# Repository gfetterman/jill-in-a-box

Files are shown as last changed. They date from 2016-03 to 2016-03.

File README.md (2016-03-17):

# jill-in-a-box
Audio filtering for the Intan EVAL board ADC inputs

The Intan EVAL board ADC accepts 0 to +3.3V inputs. Jill-in-a-box takes audio signals (+/-3.3V), raises their zero to +1.15V, constrains their amplitude to fit between 0 and +3.3V, and applies a 10kHz anti-aliasing filter.

## Version history
* v1.2: anti-aliaising filter passive components changed to use more common components. Filter cutoff is still 10kHz. Specific changes:
  * R25, R26, R27, R28, R29, R30, R31, R32: were 10kOhm, now 39kOhm
  * C14, C18, C19, C21: were 1000pF, now 270pF
  * C13, C17, C20, C22: were 2000pF, now 560pF
* v1.1: added 2-pole Butterworth anti-aliasing filter, cutoff 10kHz, on each channel
* v1.0: first production version

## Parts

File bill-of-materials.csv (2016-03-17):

Digikey part number | description | quantity
ED1516-ND | TERMINAL BLOCK 3.5MM 4POS PCB | 1
ED2741-ND | TERMINAL BLOCK 3.5MM 3POS PCB | 1
CP-3523SJTR-ND | CONN AUDIO JACK 3.5MM STEREO SMD | 4
LMC6484IN/NOPB-ND | IC OPAMP GP 1.5MHZ RRO 14DIP | 3
RNF14FTD20K0CT-ND | RES 20K OHM 1/4W 1% AXIAL | 8
CF14JT10K0CT-ND | RES 10K OHM 1/4W 5% CARBON FILM | 12
CF14JT39K0CT-ND | RES 39K OHM 1/4W 5% CARBON FILM | 8
CF14JT300RCT-ND | RES 300 OHM 1/4W 5% CARBON FILM | 4
BC1025CT-ND | CAP CER 1000PF 50V 5% RADIAL | 4
BC1018CT-ND | CAP CER 270PF 50V 5% RADIAL | 4
BC1013CT-ND | CAP CER 100PF 50V 5% RADIAL | 4
BC1084CT-ND | CAP CER 0.1UF 50V 10% RADIAL | 6
BC1022CT-ND | CAP CER 560PF 50V 5% RADIAL | 4
H342-ND | Screws 440 | 4
36-8714-ND | Standoffs 440 | 4

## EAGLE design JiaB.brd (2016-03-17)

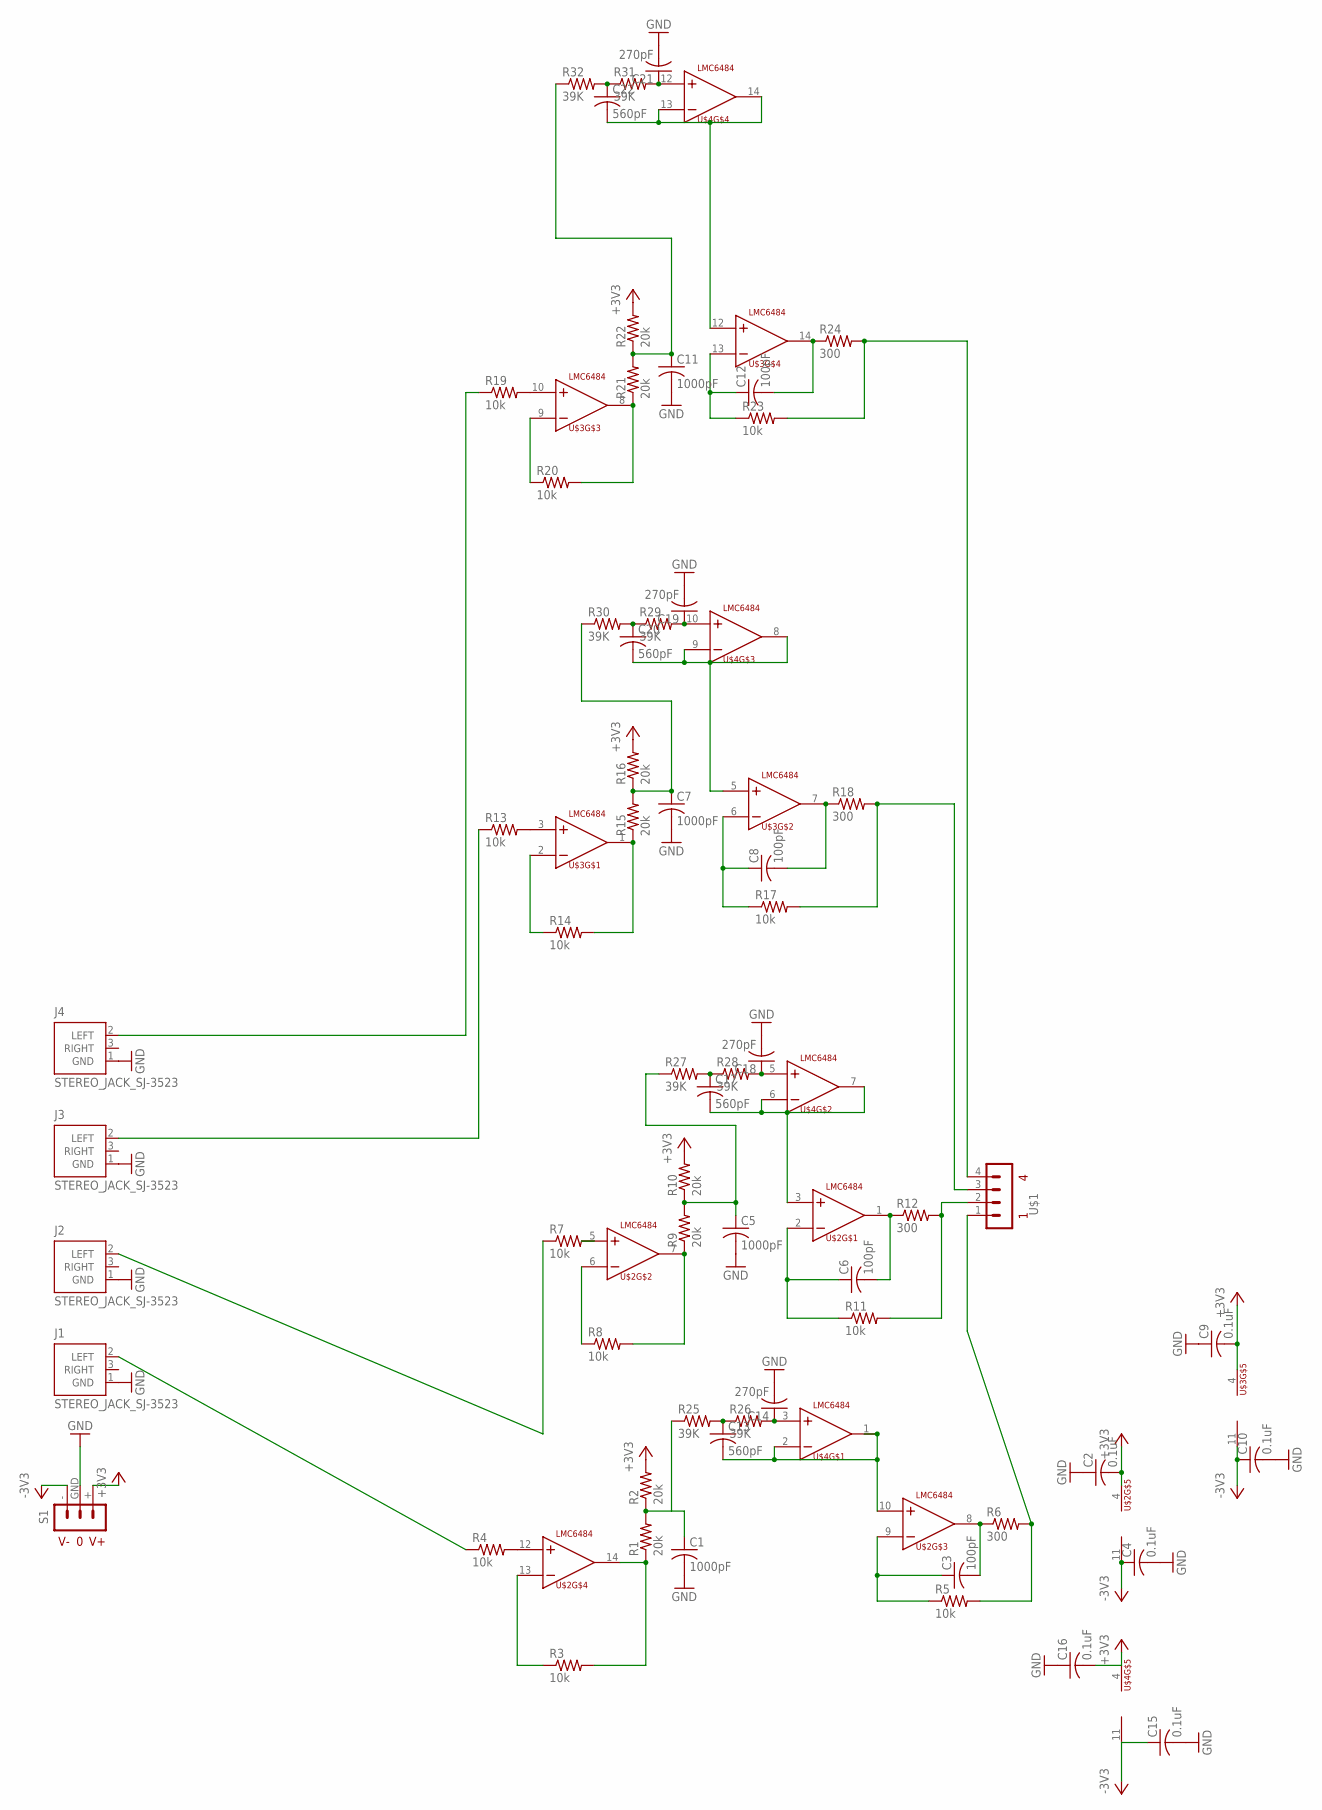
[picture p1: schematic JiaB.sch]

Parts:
C1, C5, C7, C11: 1000pF; C025-025X050
C2, C4, C9, C10, C15, C16: 0.1uF; C025-025X050
C3, C6, C8, C12: 100pF; C025-025X050
C13, C17, C20, C22: 560pF; C025-025X050
C14, C18, C19, C21: 270pF; C025-025X050
J1, J2, J3, J4: STEREO_JACK_SJ-3523; SJ-3523
R1, R2, R9, R10, R15, R16, R21, R22: 20k; 0204/7
R3, R4, R5, R7, R8, R11, R13, R14, R17, R19, R20, R23: 10k; 0204/7
R6, R12, R18, R24: 300; 0204/7
R25, R26, R27, R28, R29, R30, R31, R32: 39K; 0204/7
S1: TERMINAL_BLOCK_3_+/-3.3V; TERMINAL_BLOCK_3.5MM_3
U$1: TERMINAL-BLOCK-4
U$2, U$3, U$4: LMC6484; DIL14

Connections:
+3V3: C2.2, C9.2, C16.2, R2.2, R10.2, R16.2, R22.2, S1.+, U$2.4 (VCC+), U$3.4 (VCC+), U$4.4 (VCC+)
-3V3: C4.1, C10.1, C15.1, S1.-, U$2.11 (VCC-), U$3.11 (VCC-), U$4.11 (VCC-)
GND: C1.2, C2.1, C4.2, C5.2, C7.2, C9.1, C10.2, C11.2, C14.2, C15.2, C16.1, C18.2, C19.2, C21.2, J1.1 (GND), J2.1 (GND), J3.1 (GND), J4.1 (GND), S1.GND
unnamed: J1.2 (LEFT), R4.1
unnamed: J2.2 (LEFT), R7.1
unnamed: J3.2 (LEFT), R13.1
unnamed: J4.2 (LEFT), R19.1
unnamed: R1.1, R3.2, U$2.14 (OUT)
unnamed: C1.1, R1.2, R2.1, R25.1
unnamed: R4.2, U$2.12 (IN+)
unnamed: C3.2, R6.1, U$2.8 (OUT)
unnamed: R3.1, U$2.13 (IN-)
unnamed: R7.2, U$2.5 (IN+)
unnamed: R5.2, R6.2, U$1.1
unnamed: R8.2, R9.1, U$2.7 (OUT)
unnamed: C3.1, R5.1, U$2.9 (IN-)
unnamed: C5.1, R9.2, R10.1, R27.1
unnamed: C6.2, R12.1, U$2.1 (OUT)
unnamed: R8.1, U$2.6 (IN-)
unnamed: C6.1, R11.1, U$2.2 (IN-)
unnamed: R11.2, R12.2, U$1.2
unnamed: R13.2, U$3.3 (IN+)
unnamed: R14.2, R15.1, U$3.1 (OUT)
unnamed: C7.1, R15.2, R16.1, R30.1
unnamed: C8.2, R18.1, U$3.7 (OUT)
unnamed: R14.1, U$3.2 (IN-)
unnamed: C8.1, R17.1, U$3.6 (IN-)
unnamed: R17.2, R18.2, U$1.3
unnamed: R19.2, U$3.10 (IN+)
unnamed: R20.2, R21.1, U$3.8 (OUT)
unnamed: C11.1, R21.2, R22.1, R32.1
unnamed: C12.2, R24.1, U$3.14 (OUT)
unnamed: R20.1, U$3.9 (IN-)
unnamed: C12.1, R23.1, U$3.13 (IN-)
unnamed: R23.2, R24.2, U$1.4
unnamed: C14.1, R26.2, U$4.3 (IN+)
unnamed: C13.2, U$2.10 (IN+), U$4.1 (OUT), U$4.2 (IN-)
unnamed: C18.1, R28.2, U$4.5 (IN+)
unnamed: C13.1, R25.2, R26.1
unnamed: C17.1, R27.2, R28.1
unnamed: C17.2, U$2.3 (IN+), U$4.6 (IN-), U$4.7 (OUT)
unnamed: C19.1, R29.2, U$4.10 (IN+)
unnamed: C20.1, R29.1, R30.2
unnamed: C20.2, U$3.5 (IN+), U$4.8 (OUT), U$4.9 (IN-)
unnamed: C21.1, R31.2, U$4.12 (IN+)
unnamed: C22.1, R31.1, R32.2
unnamed: C22.2, U$3.12 (IN+), U$4.13 (IN-), U$4.14 (OUT)

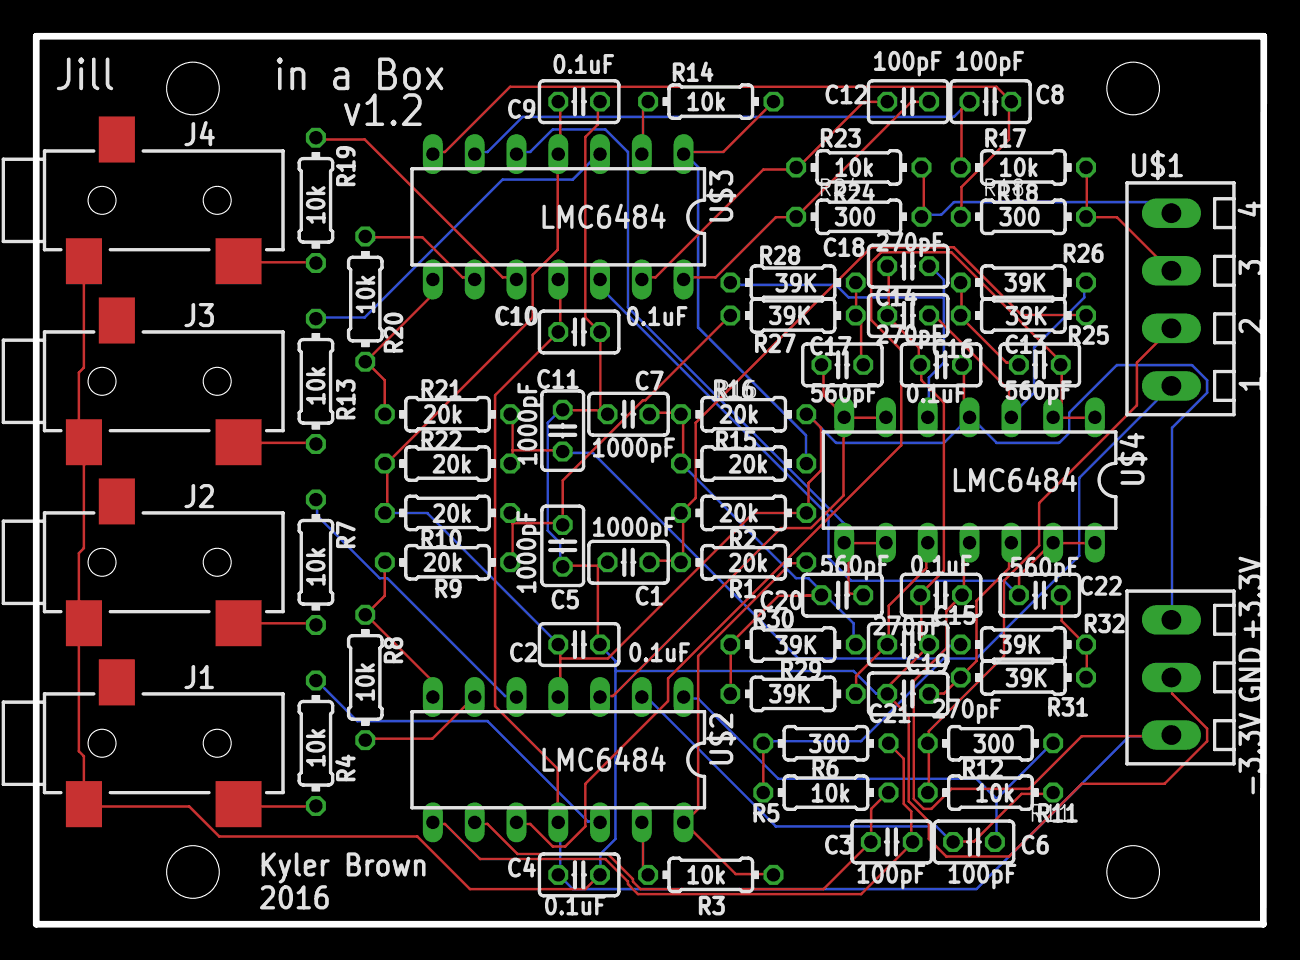
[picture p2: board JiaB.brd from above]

Board: 2 copper layers, 74.6 x 54.0 mm, 63 parts (0 on the bottom side), 47 nets.
